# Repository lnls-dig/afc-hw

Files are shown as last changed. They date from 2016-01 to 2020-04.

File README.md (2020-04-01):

# AMC FMC Carrier (AFC)

## Project description

The AMC FMC carrier is partially based on SPEC (supply, WR clocks)
design. It was primarily specified by the Brazilian Synchrotron Light
Laboratory ([LNLS](www.lnls.br)) and designed by Warsaw University of
Technology (WUT) to support quad 16-bit ADC FMC boards for Sirius BPM
electronics. Among many features, the card has very flexible clock
circuit that enables any clock source to be connected to any clock
input, including telecom clock, FMC clocks and
FPGA.

-----

Top view

Bottom view)

-----

## Functional specifications

  - Xilinx Artix-7 200T FFG1156 FPGA (XC7A200T-3FFG1156E)
  - 2 GB DDR3 SDRAM (32-bit interface)
  - 2 high pin count (HPC) slots for 2 single width mezzanines or 1
    double width mezzanine
  - SPI Flash for FPGA configuration
  - SPI Flash for user data storage
  - JTAG multiplexer (SCANSTA) for FMC access
  - Power supply for FPGA, memory, FMCs - programmable VADJ 1.8-3.3V
  - Clock distribution circuit compatible with WR
  - Temperature, voltage and current monitoring for critical power buses
  - Stand-alone power connector
  - Mini-USB connected to the IPMI processor
  - SATA connector for Port2, Port3 with possibility of switching to
    FPGA MGT
  - MGT connected to FMC1, FMC2, Fat Pipe 1, Fat Pipe 2 (optional),
    Port0, Port1, Port2 (optional), Port3 (optional), RTM (optional)
  - EEPROM with MAC and unique ID
  - RTM connector with 8 GTP routed to it. Compatible with rtm-sfp8
    module.

<!-- end list -->

  - [Users](Users)
  - [CERN-ACC-2014-0357](https://cds.cern.ch/record/1977919/files/CERN-ACC-2014-0357.pdf)

-----

## Contacts

### Commercial producers

  - [AMC FMC Carrier – AFC](http://creotech.pl/product-scientific/amc-fmc-carrier-afc) - [Creotech](http://creotech.pl), Poland

### General question about project

  - [Daniel Tavares (LNLS)](mailto:daniel.tavares@lnls.br)
  - [Filip Świtakowski (Creotech)](mailto:filip.switakowski@creotech.pl)

-----

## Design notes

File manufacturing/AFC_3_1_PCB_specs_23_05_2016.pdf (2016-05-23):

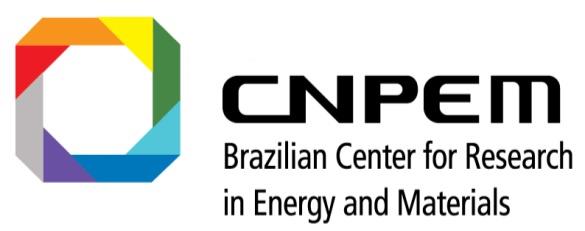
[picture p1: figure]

### Centro Nacional de Pesquisa em Energia e Materiais (CNPEM) Laboratório Nacional de Luz Síncrotron (LNLS) Rua Giuseppe Maximo Scolfaro, 10000, Polo II de Alta Tecnologia Campinas, São Paulo, Brazil CEP 13083-970 – Caixa Postal 6192

# Manufacturing specifications for the AFC_3.1 hardware

# May 2016

# Beam Diagnostics Group (DIG)

BLANK PAGE

Last update: 23 May 2016 - 18:16 | 3

## PCB Fabrication Specification

## Design references

Name | AFC_3.1 | Date: | 05/23/2015
File name
Designers | Fernando Cambauva SantAnna
E-mail | fernando.santanna@lnls.br
Fone | +55 19 3512-5071
Cel | +55 16 99206-8595

## Mechanical characteristics

External size (mm) | 180.6508mm x 148.5508mm
Thickness (mm) | 1.712 mm
Layers | 14
Min track width (mm/mils) | 0.02mm / 2mils
Min Hole size (mm/mils) | 0.15mm / 7.8mils
Laminate | FR-4 – TG150
Pre-preg | FR-4 – TG150

## Finish Copper

External layers (µm) | 35 µm
Holes walls (µm) | 25 µm
Internal Layers-Planes (µm) | 35 µm
Internal Layers-Signals (µm) | 35 µm

## Board finishing requirements

Mask Solder color | Red for prototype and Blue for production
Silkscreen on top layer (color) | White
Silkscreen on bottom layer (color) | White
Surface Finishing | ENIG – Electroless Nickel / Immersion Gold according to IPC-4552
Thickness | Ni: 3 µm min, 6 µm máx. Au: 0.05 µm min, 0.125 µm máx

## Additional Information

Impedance test | No
Packaging requirements | No
Documentation to be delivered | No
Additional control quality requirements | No

| Board Stackup Information

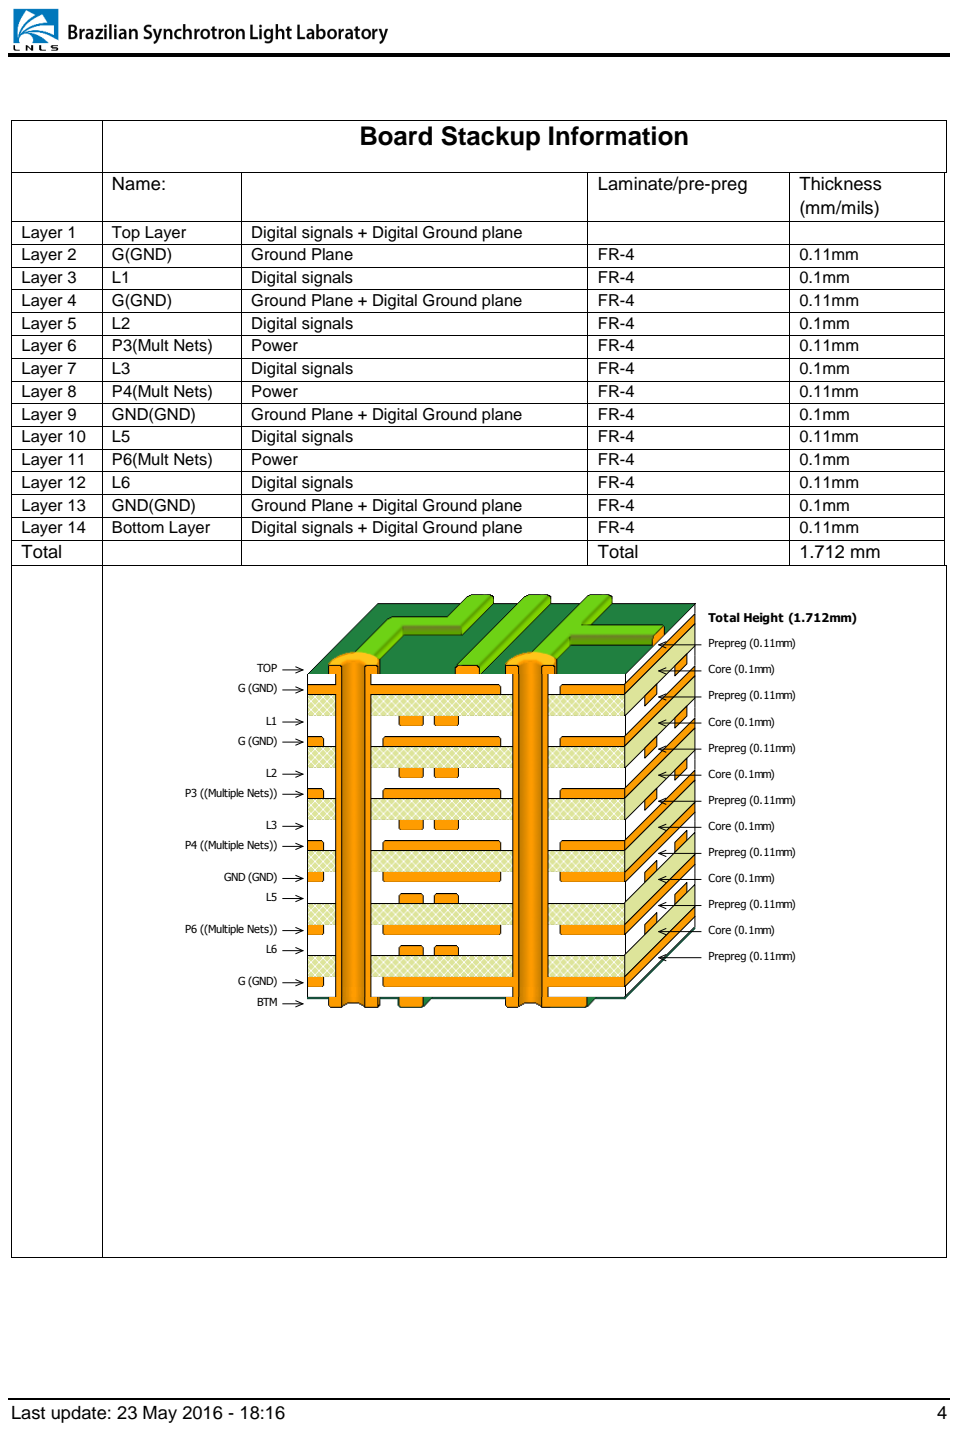
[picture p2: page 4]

Name: | | Laminate/pre-preg | Thickness (mm/mils)

Layer 1 | Top Layer | Digital signals + Digital Ground plane
Layer 2 | G(GND) | Ground Plane | FR-4 | 0.11mm
Layer 3 | L1 | Digital signals | FR-4 | 0.1mm
Layer 4 | G(GND) | Ground Plane + Digital Ground plane | FR-4 | 0.11mm
Layer 5 | L2 | Digital signals | FR-4 | 0.1mm
Layer 6 | P3(Mult Nets) | Power | FR-4 | 0.11mm
Layer 7 | L3 | Digital signals | FR-4 | 0.1mm
Layer 8 | P4(Mult Nets) | Power | FR-4 | 0.11mm
Layer 9 | GND(GND) | Ground Plane + Digital Ground plane | FR-4 | 0.1mm
Layer 10 | L5 | Digital signals | FR-4 | 0.11mm
Layer 11 | P6(Mult Nets) | Power | FR-4 | 0.1mm
Layer 12 | L6 | Digital signals | FR-4 | 0.11mm
Layer 13 | GND(GND) | Ground Plane + Digital Ground plane | FR-4 | 0.1mm
Layer 14 | Bottom Layer | Digital signals + Digital Ground plane | FR-4 | 0.11mm
Total | | | Total | 1.712 mm

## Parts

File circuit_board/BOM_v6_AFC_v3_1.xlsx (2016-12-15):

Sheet: BOM_AFC_v3.1
Prj: | AFC 3.1 | REV.: 6 | data: | 2016-03-04
QTD | Description | Part-number | Manufacturer | Designator
1 | AMC front Panel Double Mid - Aluminum | AMC.0 REL. 2.0 Compliant | CBT Technology
12 | CAEM2917_150UF_4V_20%_LESR015 | EEF-CX0J151R | Panasonic | C86, C115, C135, C473, C539, C41, C50, C55, C64, C230, C231, C528
1 | CAER_470UF_16V_20%_500-1000X1300 | PLF1C471MDO1 | Nichicon | C88
17 | CC0201_0.022UF_6.3V_10%_X5R | GRM033R60J223KE01D | Murata Electronics | C251, C252, C253, C254, C259, C418, C599, C600, C601, C722, C723, C724, C725, C730, C731, C732, C733
376 | CC0201_0.1UF_10V_10%_X5R | GRM033R61A104KE15D | Murata Electronics | C4A, C4B, C6A, C6B, C10A, C10B, C11A, C11B, C15A, C15B, C20, C21, C22, C23, C24, C25, C26, C27, C28, C29, C30, C31, C38, C39, C52, C56, C57, C58, C59, C61, C63, C65, C67, C69, C70, C73, C74, C75, C76, C78, C80, C82, C83, C84, C89, C93, C94, C95, C96, C98, C99, C100, C101, C102, C103, C104, C105, C109, C110, C111, C112, C114, C118, C120, C121, C124, C125, C128, C129, C131, C132, C134, C138, C140, C141, C219, C220, C221, C222, C223, C224, C225, C227, C228, C255, C256, C257, C258, C262, C263, C273, C274, C281, C282, C289, C290, C297, C298, C299, C300, C301, C302, C303, C304, C305, C306, C307, C308, C309, C310, C311, C312, C313, C314, C315, C316, C317, C334, C335, C336, C337, C338, C339, C340, C341, C342, C343, C344, C345, C346, C347, C348, C349, C350, C351, C352, C353, C354, C355, C356, C357, C358, C359, C360, C361, C362, C363, C364, C365, C366, C367, C368, C369, C370, C371, C372, C373, C374, C375, C376, C377, C378, C379, C380, C381, C382, C383, C384, C385, C386, C387, C388, C389, C391, C392, C393, C394, C395, C396, C397, C398, C399, C400, C401, C402, C403, C404, C405, C406, C407, C408, C409, C410, C411, C412, C413, C414, C415, C417, C421, C422, C424, C425, C427, C428, C429, C430, C431, C432, C433, C434, C436, C437, C438, C439, C440, C441, C442, C443, C452, C455, C457, C458, C459, C460, C461, C462, C463, C464, C476, C477, C479, C480, C481, C482, C483, C484, C485, C486, C487, C488, C489, C490, C491, C492, C493, C494, C495, C496, C497, C498, C499, C500, C501, C502, C503, C504, C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
71 | CC0201_0.22UF_6.3V_20%_X5R | C0603X5R0J224M030BB | TDK Corporation | C229, C232, C233, C234, C235, C236, C239, C240, C241, C242, C243, C244, C245, C246, C247, C248, C249, C250, C264, C265, C266, C269, C270, C271, C275, C276, C277, C278, C279, C280, C283, C284, C285, C286, C287, C288, C291, C292, C293, C294, C295, C296, C549, C550, C551, C552, C553, C554, C555, C556, C557, C558, C559, C560, C561, C562, C563, C564, C565, C566, C738, C739, C740, C741, C742, C743, C744, C745, C746, C747, C748
62 | CC0201_0.47UF_6.3V_20%_X5R | C0603X5R0J474M030BC | TDK Corporation | C260, C261, C448, C449, C450, C451, C465, C603, C613, C614, C615, C639, C640, C641, C642, C643, C647, C648, C649, C650, C651, C655, C656, C657, C658, C659, C663, C664, C665, C666, C667, C671, C672, C673, C674, C675, C683, C684, C685, C686, C687, C691, C692, C693, C694, C695, C699, C700, C701, C702, C703, C707, C708, C709, C710, C711, C716, C717, C718, C719, C720, C721
7 | CC0402_0.1UF_16V_10%_X7R | GRM155R71C104KA88D | Murata Electronics | C77, C113, C133, C159, C470, C527, C538
3 | CC0402_10000PF_16V_10%_X7R | GRM155R71C103KA01D | Murata Electronics | C35, C60, C547
3 | CC0402_1000PF_50V_10%_X7R | GRM155R71H102KA01D | Murata Electronics | C166, C634, C635
1 | CC0402_15PF_50V_5%_NPO | CC0402JRNPO9BN150 | Yageo | C208, C435, C444
2 | CC0402_22PF_50V_5%_NPO | CC0402JRNPO9BN220 | Yageo | C18, C19
1 | CC0603_0.022UF_50V_10%_X7R | C1608X7R1H223K080AA | TDK Corporation | C160
2 | CC0603_150PF_50V_5%_NP0 | GRM1885C1H151JA01D | Murata Electronics | C33, C53
54 | CC0603_1UF_25V_10%_X7R | TMK107B7105KA-T | Taiyo Yuden | C2A, C2B, C3A, C3B, C8A, C8B, C9A, C9B, C13A, C13B, C14A, C14B, C16A, C16B, C17A, C17B, C32, C44, C49, C51, C62, C68, C72, C90, C91, C92, C108, C126, C127, C130, C143, C144, C145, C153, C209, C210, C390, C416, C426, C453, C468, C469, C475, C526, C532, C535, C537, C543, C622A, C622B, C623A, C623B, C816, C817
59 | CC0603_4.7UF_10V_10%_X5R | CC0603KRX5R6BB475 | Yageo | C106, C107, C237, C238, C267, C268, C272, C446, C478, C576, C577, C578, C579, C580, C581, C582, C583, C585, C586, C588, C589, C591, C594, C596, C597, C598, C605, C606, C607, C608, C609, C610, C611, C636, C637, C644, C645, C646, C652, C653, C654, C660, C661, C662, C668, C669, C670, C680, C681, C682, C688, C689, C690, C696, C697, C698, C704, C705, C706
24 | CC0805_10UF_25V_10%_X5R | GRM21BR61E106KA73L | Murata Electronics | C12A, C12B, C34, C40, C42, C43, C45, C48, C54, C66, C97, C146, C147, C148, C149, C150, C151, C152, C167, C466, C467, C525, C533, C536
62 | CC1206_22UF_10V_10%_X7R | LMK316AB7226KL-TR | Taiyo Yuden | C1A, C1B, C5A, C5B, C7A, C7B, C46, C47, C71, C79, C81, C85, C87, C116, C117, C119, C122, C123, C136, C137, C139, C142, C154, C155, C156, C157, C158, C161, C162, C163, C164, C165, C168, C169, C170, C171, C172, C173, C174, C175, C176, C177, C419, C420, C423, C454, C455a, C455b, C456, C471, C472, C474, C529, C530, C531, C534, C540, C541, C542, C544, C545, C546
16 | CC1210_100UF_10V_20%_X5R | GRM32ER61A107ME20L | Murata Electronics | C226, C447, C587, C592, C593, C602, C612, C638, C676, C677, C678, C679, C712, C713, C714, C715
1 | CONN GUIDE MODULE KEYED 1POS | 5120913-1 | TE Connectivity AMP Connectors | J12
1 | CONN HDR 2X5 0.100" SMT | 54202-G0805LF | FCI | JP1
1 | CONN HEADER .050" 2X5 DL PCB AU | GRPB052VWVN-RC | Sullins Connector Solutions | JP2
1 | CONN HEADER 14POS 2MM VERT SMD | 87832-1420 | Molex | J6
1 | CONN HEADER 4POS 4.2MM VERT TIN | 39-28-1043 | Molex | J4
2 | CONN RCPT 60POS 3PAIR R/A HM-ZD | 6469081-1 | TE Connectivity AMP Connectors | J1, J2
2 | CONN RCPT STD MICRO USB TYPE AB | 10104111-0001LF | FCI | CON2A, CON2B
4 | CONN UMC JACK STR 50 OHM SMD | U.FL-R-SMT-1(10) | Hirose Electric | J7, J11, J16, J17
2 | CONN, VITA 57 FMC, RCPT, 400POS, 10ROW | ASP-134486-01 | SAMTEC | J15A, J15B
1 | CRYSTAL 32.7680KHZ 12.5PF SMD | ABS25-32.768KHZ-T | Abracon | X3
3 | DIODE SCHOTTKY 40V 750MA SOD323 | BAT165E6327 | Infineon Technologies | D1, D3, D4
3 | DIODE SCHOTTKY 60V 1A DO214AC | SS16-E3/61T | Vishay | D2, D5, D6
1 | F_PTC_9.5x6mm | MF-SM250-2-99 | Bourns Inc. | F3
4 | FERRITE BEAD 100 OHM 8A SMD 1812 | 74279226101 | Wurth Electronics | FB5, FB6, FB7, FB8
6 | FERRITE CHIP 220 OHM 0805 | BLM21PG221SN1D | Murata Electronics | L9, L14, L17, L18, L19, L21
6 | FIXED IND 1.5UH 11A 10.67 MOHM | SPM6530T-1R5M100 | TDK Corporation | L1, L3, L5, L6, L15, L16
4 | FIXED IND 1UH 1.8A 52 MOHM SMD | ELLVGG1R0N | Panasonic Electronic | L10, L11, L12, L13
2 | FIXED IND 3.3UH 5.3A 15 MOHM SMD | 74456033 | Wurth Electronics | L2, L7
1 | FIXED IND 440NH 30A 0.32 MOHM | PA0513.441NLT | Pulse Electronics | L8
1 | Heat sink BGA 35x35(44.9)mm | ATS-50350B-C1-R0 | Advanced Thermal Solutions | HS1
2 | IC BUS TRANSCVR 8BIT 24QFN | SN74AVC8T245RHLR | Texas Instruments | IC40, IC41
8 | IC BUS TRANSCVR TRI-ST SOT-563 | SN74AVC1T45DRLR | Texas Instruments | IC28, IC29, IC34, IC35, IC36, IC37, IC38, IC39
1 | IC CLK GEN 1:4 LOW JITTER 32-QFN | CDCM61004RHBT | Texas Instruments | IC50
1 | IC CROSSPOINT SWIT 16X16 100TQFP | ADN4604ASVZ | Analog Devices | IC8
6 | IC CURRENT MONITOR 1% 10MSOP | INA220AIDGST | Texas Instruments | IC19, IC20, IC21, IC59, IC60, IC61
2 | IC DAC 16BIT BUFF V-OUT 8MSOP | AD5662BRMZ-1 | Analog Devices | IC52, IC53
1 | IC EEPROM 2KBIT 1MHZ 8TSSOP | AT24MAC602-XHM-T | Atmel | IC27
2 | IC FLASH 128MBIT 50MHZ 8VDFPN | M25P128-VME6TGB | Micron Technology | IC13, IC64
1 | IC FPGA 500 I/O 1156FCBGA | XC7A200T-3FFG1156E | Xilinx | IC2
1 | IC MCU ARM 128KB FLASH 100LQFP | LPC1764FBD100 | NXP Semiconductors | IC1
2 | IC M-LVDS RCVR QUAD 48VQFN | SN65MLVD040RGZT | Texas Instruments | IC22, IC23
1 | IC MPU RESET CIRC 2.93V SOT143-4 | PT7M7811STBEX | Pericom | IC58
1 | IC MPU RESET CIRC 2.93V SOT23 | STM809SWX6F | STMicroelectronics | IC3
1 | IC MUX 8CH I2C BUS 24-HVQFN | PCA9547BS,118 | NXP Semiconductors | IC79
2 | IC MUX UHS NONINVERT 2INP SC70-6 | NC7SZ157P6X | Fairchild Semiconductor | IC80, IC81
1 | IC MUX/DEMUX TRIPLE 2X1 16SOIC | 74HC4053D,653 | NXP Semiconductors | IC73
1 | IC POT DGTL DUAL 10K 8BIT 14SOIC | AD8402ARZ1 | Analog Devices | IC11
1 | IC REDRIVER I2C 1CH 8VSSOP | PCA9517DGKR | Texas Instruments | IC42
4 | IC REDRIVER LVDS 1CH 1.6GBPS US8 | FIN1101K8X | Fairchild Semiconductor | IC46, IC47, IC49, IC66
1 | IC REG BUCK ADJ 20A SYNC 22SON | TPS53353DQPT | Texas Instruments | IC14
2 | IC REG BUCK ADJ 3A SYNC 8SOIC | NCP3170ADR2G | ON Semiconductor | IC55, IC57
3 | IC REG CTRLR BUCK PWM 24-VQFN | TPS53126RGET | Texas Instruments | IC10, IC12, IC43
1 | IC REG LDO 3.3V 0.8A DPAK | LD1117DT33CTR | STMicroelectronics | IC74
1 | IC REG LDO 3V 0.15A SOT23-5 | LP5951MF-3.0/NOPB | Texas Instruments | IC51
1 | IC RTC CLK/CALENDAR I2C 8-SOIC | MCP79410-I/SN | Microchip Technology | IC9
1 | IC SCAN BRIDGE MULTIDROP 48TSSOP | SCANSTA111MT/NOPB | Texas Instruments | IC6
1 | IC SINK/SOURCE DDR REG 10-SON | TPS51200DRCT | Texas Instruments | IC44
2 | IC USB-TO-UART BRIDGE 28VQFN | CP2102-GM | Silicon Labs | IC62A, IC62B
4 | IC VOLT-LEVEL TRANSLATOR 14TSSOP | TXB0104PWR | Texas Instruments | IC68, IC69, IC70, IC71
2 | IC VOLT-LEVEL TRANSLATOR SM8 | PCA9306DCTR | Texas Instruments | IC25, IC56
1 | IC VREF SHUNT ADJ SOT23-3 | TS3431ILT | STMicroelectronics | IC45
1 | IC VREF SHUNT ADJ SOT23-3 | TL431QDBZT | Texas Instruments | IC54
1 | LED CHIP GREEN CLEAR RA 0603 SMD | HSME-C120 | Avago Technologies | LDx
1 | LED CHIP INGAN BLU SIDE EMIT SMD | HSMR-C120 | Avago Technologies | LDy
15 | LED CHIP RED CLEAR RT ANG 0603 SMD | HSMC-C120 | Avago Technologies | LED3, LED4, LED5, LED6, LED7, LED8, LED9, LED10, LED11, LED12, LED13, LED14, LED15, LED16, LED17
1 | LED RED/GRN/BLUE 1204 SMD | OVSRRGBCC3TM | TT Electronics | LD1
4 | MEM Chip DDR3 SDRAM 4G-Bit 512Mx8 1.35V(1.5 Compatibile) 78-Pin FBGA | MT41K512M8RH-125:E | MT41K512M8RH-125:E | IC15, IC16, IC24, IC26
6 | MOSFET 2N-CH 20V 10A/12A 8-SOIC | IRF9910TRPbF | Infineon Technologies | T1, T2, T3, T4, T5, T6
7 | MOSFET N-CH 50V 220MA SOT-23 | BSS138 | Fairchild Semiconductor | Q3, Q4, Q7, Q9, Q10, Q11, Q14
3 | MOSFET P-CH 30V 20A 8-SOIC | IRF9310TRPbF | Infineon Technologies | Q1, Q2, Q13
1 | OSC XO 10-280MHZ LVPECL SMD | Si570BBC000121DG | Silicon Labs | OSC4
1 | OSC_20MHZ_IQD_LF VCXO026156 | LF VCXO026156 | IQD FREQUENCY PRODUCTS | OSC2
3 | PTC SMD 1812 0.5A 16V | PTS181216V050 | Eaton Bussman | F1, F2, F4
1 | Quartz crystal SMD 5*3.2mm 8.000MHz | 7A-8.000MAAJ-T | TXC | X1
2 | R0201_49R9_1%_0.05W_200PPM | ERJ-1GEF49R9C | Panasonic Electronic | R143, R181
18 | R0402_0R_JUMPER_0.1W | RC0402JR-070RL | Yageo | R70, R80, R124, R135, R136, R137, R139, R140, R146, R215, R253, R258, R289, R290, R293, R306, R318, R319
15 | R0402_100K_1%_0.0625W_100PPM | RC0402FR-07100KL | Yageo | R45, R52, R64, R106, R109, R110, R120, R121, R179, R209, R210, R269, R297, R301, R302
37 | R0402_100R_1%_0.0625W_100PPM | RC0402FR-07100RL | Yageo | R7, R8, R9, R10, R11, R12, R13, R14, R15, R16, R17, R18, R96, R118, R142, R148, R149, R150, R151, R152, R153, R154, R155, R156, R157, R207, R208, R217, R226, R227, R229, R230, R231, R239, R335, R345, R346
60 | R0402_10K_1%_0.0625W_100PPM | RC0402FR-0710KL | Yageo | R2, R3, R4, R5, R6, R19, R37, R38, R39, R40, R55, R57, R58, R59, R60, R61, R71, R78, R79, R82, R85, R92, R97, R98, R99, R100, R101, R102, R103, R104, R105, R114, R117, R122, R123, R141, R145, R147, R158, R159, R162, R164, R180, R222, R225, R238, R246, R255, R264, R265, R268, R270, R280, R281, R282, R305, R309, R310, R326, R350
16 | R0402_10R_1%_0.0625W_100PPM | RC0402FR-0710RL | Yageo | R125, R126, R129, R130, R133, R286, R291, R292, R294, R295, R296, R298, R300, R303, R304, R351
12 | R0402_1K_1%_0.0625W_100PPM | RC0402FR-071KL | Yageo | R165, R220, R221, R232, R233, R234, R235, R236, R237, R272, R287, R288
3 | R0402_1K3_1%_0.1W_100PPM | ERJ-2RKF1301X | Panasonic Electronic | R54, R86, R91
7 | R0402_240R_1%_0.0625W_100PPM | RC0402FR-07240RL | Yageo | R144, R167, R168, R216, R218, R219, R228
34 | R0402_2K2_1%_0.0625W_100PPM | RC0402FR-072K2L | Yageo | R36, R47, R81, R83, R119, R169, R170, R171, R172, R173, R174, R176, R178, R214, R244, R271, R273A, R273B, R274A, R274B, R275A, R275B, R276A, R276B, R283, R307, R308, R313, R314, R331, R332, R338, R347, R348
11 | R0402_330R_1%_0.0625W_100PPM | CRCW0402330RFKED | Vishay Dale | R23, R24, R132, R161, R175, R213, R277, R278, R279, R311, R312
4 | R0402_33R_1%_0.0625W_100PPM | RC0402FR-0733RL | Yageo | R284A, R284B, R285A, R285B
27 | R0402_43R_1%_0.0625W_100PPM | CRCW040243R0FKED | Vishay Dale | R163, R177, R182, R183, R184, R185, R186, R187, R188, R189, R190, R191, R192, R193, R194, R195, R196, R197, R198, R199, R200, R201, R202, R203, R204, R205, R206
2 | R0402_49R9_1%_0.0625W_100PPM | CRCW040249R9FKED | Vishay Dale | R51, R211
10 | R0402_4K7_1%_0.0625W_100PPM | RC0402FR-074K7L | Yageo | R20, R21, R22, R49, R50, R69, R127, R131, R160, R166
8 | R0402_510R_1%_0.0625W_100PPM | RC0402FR-07510RL | Yageo | R65, R66, R74, R76, R77, R88, R93, R256
1 | R0603_169K_1%_0.1W_100PPM | CRCW0603169KFKEA | Vishay Dale | R112
3 | R0603_1K5_1%_0.1W_100PPM | RC0603FR-071K5L | Yageo | R46, R247, R248
1 | R0603_1K6_1%_0.1W_100PPM | CRCW06031K60FKEA | Vishay Dale | R48
2 | R0603_24K9_0.1%_0.0625W_10PPM | PCF0603-12-24K9BT1 | TT Electronics/Welwyn | R43, R62
2 | R0603_2K49_0.1%_0.0625W_25PPM | RNCS0603BKE2K49 | Stackpole Electronics Inc. | R44, R63
3 | R0603_2R_1%_0.1W_200PPM | RC0603FR-072RL | Yageo | R111, R327, R328
3 | R0603_3K3_1%_0.1W_100PPM | RC0603FR-073K3L | Yageo | R72, R115, R116
2 | R0603_453R_0.1%_0.1W_25PPM | RG1608P-4530-B-T5 | Susumu | R262, R263
3 | R0603_4K3_1%_0.1W_100PPM | RC0603FR-074K3L | Yageo | R53, R84, R90
7 | R0603_5K1_1%_0.1W_100PPM | RC0603FR-075K1L | Yageo | R41, R42, R73, R87, R95, R223, R259
1 | R0603_75K_1%_0.1W_100PPM | ERJ-3EKF7502V | Panasonic Electronic | R108
2 | R0603_910R_1%_0.1W_100PPM | ERJ-3EKF9100V | Panasonic Electronic | R260, R261
2 | R1206_100K_1%_0.25W_100PPM | ERJ-8ENF1003V | Panasonic Electronic | R320, R321
1 | R1206_3R_1%_0.25W_200PPM | RC1206FR-073RL | Yageo | R113
8 | R2512_0.001R_1%_2W_275PPM | WSL25121L000FEA | Vishay Dale | R75, R89, R94, R257, R266, R267
4 | SENSOR TEMPERATURE I2C 8SOIC | LM75AIM/NOPB | Texas Instruments | IC30, IC31, IC32, IC33
1 | SENSOR TEMPERATURE SMBUS 6TDFN | MAX6642ATT90-T | Maxim Integrated | IC18
1 | SWITCH DETECTOR SPST TOP ACT 5V | HDT0001 | C&K Components | PB1
1 | SWITCH TACTILE Push Button 6X6mm | SKHHLQA010 | ALPS | S1
3 | TRANS NPN 45V 0.1A SOT-23 | BC847B,215 | NXP Semiconductors | Q5, Q6, Q12
2 | TVS DIODE 5.5VWM SOT143B | PRTR5V0U2X,215 | NXP Semiconductors | D7A, D7B
3 | TVS DIODE 6.2VWM 9VC 6TSOP | BZA462A,115 | NXP Semiconductors | IC4, IC5, IC7
1 | VC-TCXO SMD 3V 25.000MHz 3.2x5mm | VM53S3-25.000-2.5/-30+75 | Mercury | OSC5

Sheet: Plan1
C4A
C4B
C6A
C6B
C10A
C10B
C11A
C11B
C15A
C15B
C20
C21
C22
C23
C24
C25
C26
C27
C28
C29
C30
C31
C38
C39
C52
C56
C57
C58
C59
C61
C63
C65
C67
C69
C70
C73
C74
C75
C76
C78
C80
C82
C83
C84
C89
C93
C94
C95
C96
C98
C99
C100
C101
C102
C103
C104
C105
C109
C110
C111
C112
C114
C118
C120
C121
C124
C125
C128
C129
C131
C132
C134
C138
C140
C141
C219
C220
C221
C222
C223
C224
C225
C227
C228
C255
C256
C257
C258
C262
C263
C273
C274
C281
C282
C289
C290
C297
C298
C299
C300
C301
C302
C303
C304
C305
C306
C307
C308
C309
C310
C311
C312
C313
C314
C315
C316
C317
C334
C335
C336
C337
C338
C339
C340
C341
C342
C343
C344
C345
C346
C347
C348
C349
C350
C351
C352
C353
C354
C355
C356
C357
C358
C359
C360
C361
C362
C363
C364
C365
C366
C367
C368
C369
C370
C371
C372
C373
C374
C375
C376
C377
C378
C379
C380
C381
C382
C383
C384
C385
C386
C387
C388
C389
C391
C392
C393
C394
C395
C396
C397
C398
C399
C400
C401
C402
C403
C404
C405
C406
C407
C408
C409
C410
C411
C412
C413
C414
C415
C417
C421
C422
C424
C425
C427
C428
C429
C430
C431
C432
C433
C434
C436
C437
C438
C439
C440
C441
C442
C443
C452
C455
C457
C458
C459
C460
C461
C462
C463
C464
C476
C477
C479
C480
C481
C482
C483
C484
C485
C486
C487
C488
C489
C490
C491
C492
C493
C494
C495
C496
C497
C498
C499
C500
C501
C502
C503
C504
C505
C506
C507
C508
C509
C510
C511
C512
C513
C514
C515
C516
C517
C518
C519
C520
C521
C522
C523
C524
C548
C567
C568
C569
C570
C571
C572
C573
C574
C575
C584
C590
C595
C595x
C604
C616
C617
C618
C619
C620
C621
C624A
C624B
C625
C726
C727
C728
C729
C734
C735
C736
C737
C749
C750
C751
C752
C753
C755
C756
C757
C758
C759
C760
C762
C766
C768
C769
C770
C771
C772
C773
C774
C775
C776
C777
C778
C779
C780
C781
C782
C783
C784
C785
C786
C787
C788
C789
C790
C791
C792
C793
C794
C795
C796
C797
C798
C799
C800
C801
C802
C803
C804
C805
C806
C807
C808
C809
C810
C811
C812
C813
C814
C815
C838
C839
C875
C882
C888
CC524

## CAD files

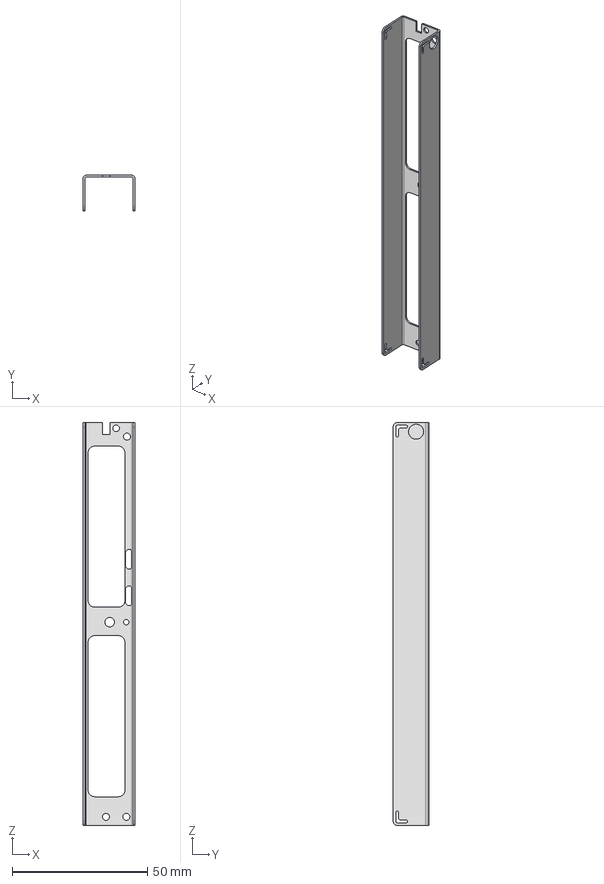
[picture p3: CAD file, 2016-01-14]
mechanical/AMC_FMC_Carrier_35u_tears.stp
19.2 x 13.2 x 148.8 mm

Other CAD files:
mechanical/AMC_PANEL_SILK.dwg
mechanical/AMC_FMC_Carrier_35u_tears.igs

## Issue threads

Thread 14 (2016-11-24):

### ISSUE TITLE
Replace D5 and D6 for a single higher forward current diode

### ISSUE THREAD

**Issue by henrique-silva** [lnls-dig/afc-hw#14]
The SS16 schottky diode has a forward current limit set in 1A, which is less than needed for the AFC board fully operate with both FMC connected when powered from the ATX stand-alone connector.

Using 2 diodes in parallel is dangerous because if they have a slight unbalacing, one of them will start to drive more current and, consequently, heat more. The heating in a diode makes it drive even more current, resulting in a positive current feedback that ends with the diode burning up.

**Comment by aylons** [comment]
I agree.

To substitute it, I suggest a diode from this list:

http://www.digikey.com/product-search/en/discrete-semiconductor-products/diodes-rectifiers-single/1376383?k=&pkeyword=&pv1291=2025&pv1291=7351&pv1291=2050&FV=1140003%2Ce480002%2Ce480006%2Ce480009%2Ce480014%2Ce48001c%2Ce480020%2Ce480023%2Ce480024%2Ce480027%2Ce480028%2Ce480029%2Ce48002f%2Ce480038%2Ce48003f%2Ce480062%2Ce4800c4%2Ce4800c7%2Ce4800c9%2Ce4800ca%2Ce4800cb%2Ce4800cd%2Ce4800cf%2Ce4800d0%2Ce4800d2%2Ce4800fa%2Ce480136%2Ce480138%2Ce480139%2Ce48016e%2Ce48016f%2Ce4801c7%2Ce500001%2Ce500002%2Ce500003%2Ce500005%2Ce500006%2Ce500007%2Ce50000a%2Ce50000b%2Ce50000c%2Ce50000d%2Ce50000e%2Ce50000f%2Ce500010%2Ce500011%2Ce500012%2Ce500013%2Ce500014%2Ce500015%2Ce500016%2Ce500017%2Ce500018%2Ce500019%2Ce50001a%2Ce50001b%2Ce50001c%2Ce50001d%2Ce50001e%2Ce50001f%2Ce500020%2Ce500021%2Ce500022%2Ce500023%2Ce500024%2Ce500025%2Ce500027%2Ce500028%2Ce500029%2Ce50002a%2Ce50002b%2Ce50002c%2Ce50002d%2Ce50002e%2Ce50002f%2Ce500030%2Ce500032%2Ce500034%2Ce500035%2Ce500037%2Ce500038%2Ce500039%2Ce50003a%2Ce50003b%2Ce50003c%2Ce50003d%2Ce50003e%2Ce50003f%2Ce500040%2Ce500041%2Ce500042%2Ce500043%2Ce500044%2Ce500045%2Ce50004a%2Ce50004e%2Ce500051%2Ce500058%2Ce50005c%2Ce500061%2Ce500063%2Ce50006b%2Ce50006e%2Ce50006f%2Ce500076%2Ce500077%2Ce500078%2Ce500079%2Ce50007a%2Ce50007b%2Ce50007e%2Ce500080%2Ce500082%2Ce500083%2Ce500084%2Ce50008b%2Ce50008c%2Ce50008f%2Ce500090%2Ce500092%2Ce500093%2Ce500094%2Ce500095%2Ce500096%2Ce500097%2Ce500098%2Ce500099%2Ce50009a%2Ce50009d%2Ce50009e%2Ce5000a0%2Ce5000a1%2Ce5000a2%2Ce5000a3%2Ce5000a4%2Ce5000a5%2Ce5000a6%2Ce5000a8%2Ce5000a9%2Ce5000aa%2Cfff40015%2Cfff8007f%2C40014d%2C400389%2C400ab1&mnonly=0&newproducts=0&ColumnSort=1000011&page=1&stock=1&quantity=0&ptm=0&fid=0&pageSize=250

I actually liked this option from AVX, which is small and fits the bill:

http://www.digikey.com/product-detail/en/avx-corporation/SD2114S040S8R0/478-7817-2-ND/3749521

However, maybe a more standard and bigger DO-214 (SMB or SMC) would be a better option, so we can change PN or manufacturer later.

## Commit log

2013-08-26 new repo initialization for rev1 and rev2 production files
    [AMC-SATA.SchDoc, AMC_Connector.SchDoc, AMC_FMC_Carrier v2.PrjPcb, AMC_FMC_Carrier v2.csv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]
2013-10-25 afc v3 init repo
    [AMC-SATA.SchDoc, AMC_Connector.SchDoc, AMC_FMC_Carrier v3.PrjPcb, AMC_FMC_Carrier.SchDoc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]
2013-11-03 fixed several issues wrong voltage measurement on FMC P12V - before the switch Added JTAG support for RTM_CON Added RTM power switches and I2C buffer moved both USB ports to the front panel swapped G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
    [AMC_FMC_Carrier.SchDoc, CPU.SchDoc, Clock_management.SchDoc, FMC_HPC1.SchDoc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]
2013-11-04 design ready for schematic review
    [AMC_FMC_Carrier v3.PrjPcb, Clock_management.SchDoc, FPGA.SchDoc, FPGA_MGT.SchDoc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]
2013-11-05 added option description to the MGT schematic detected swapped RTM connectors - some work need to be done on layout version without polygons to reduce PCB size and to make checking easier
    [AMC_Connector.SchDoc, AMC_FMC_Carrier v3.PrjPcb, FPGA_MGT.SchDoc]
2013-11-24 added low jitter WR clock output (UFL connectors) inverted all HPC lines
    [Clock_WR.SchDoc, FMC_HPC1.SchDoc, FMC_HPC2.SchDoc, FPGA_MGT.SchDoc]
2013-11-25 MGT connection upgrade - AMC Ports 12-15 added, P3V3 aux regulator added in stand-alone mode Port0/1 and 2-lane FP2 operation now possible quad 116 connected to the clock crossbar lot of small bugs f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
    [AMC-SATA.SchDoc, AMC_Connector.SchDoc, AMC_FMC_Carrier v3.PrjPcb, AMC_FMC_Carrier.SchDoc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]
2014-01-01 unified all RC All RC come from CERN library Seriously limited BOM Almost all issues solved PCB - acute angles removed improved plane layout- limited cutouts over high speed signals added OutJob file
    [AMC-SATA.SchDoc, AMC_Connector.SchDoc, AMC_FMC_Carrier v3.PrjPcb, AMC_FMC_Carrier.SchDoc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]
2014-01-29 added low jitter clock bypass
    [AMC_FMC_Carrier v3.PrjPcb, Clock_management.SchDoc, Low_jitter_CLK_bypass.SchDoc]
2014-02-10 added low jitter clock bypass - implemented on PCB
    [AMC_FMC_Carrier v3.PrjPcb, AMC_FMC_Carrier.SchDoc, CPU.SchDoc, Clock_management.SchDoc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]
2014-02-21 100% of layout done, some cosmetic changes may be needed. 0 DRC errors fixed some bugs
    [FMC_Clocks.SchDoc, Low_jitter_CLK_bypass.SchDoc]
2014-02-21 version compatible with AD10
    [AMC_FMC_Carrier.SchDoc]
2014-04-04 fixed some mechanical issues. Added OHL license on the schematics updated mounted/not mounted designators.
    [AMC-SATA.SchDoc, AMC_FMC_Carrier v3.PrjPcb, AMC_FMC_Carrier.SchDoc, Clock_management.SchDoc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]
2014-05-16 added PCB file to the commit
2014-08-01 Added schematics & pcb pdf
    [Low_jitter_CLK_bypass.SchDoc]
2015-06-03 added v.3.1
    [AMC-SATA.SchDoc, AMC_Connector.SchDoc, AMC_FMC_Carrier v2.csv, AMC_FMC_Carrier v2.xlsx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]
2016-01-14 New folder and files structure
    structure following the pattern DIG
    [AMC-SATA.SchDoc, AMC_CPU_COM_EXPRESS.igs, AMC_CPU_COM_EXPRESS.stp, AMC_CPU_COM_EXPRESS_silk.dwg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]
2016-02-05 remove mechanical design files
    leave only files related to the AFC project itself
    [AMC_CPU_COM_EXPRESS.igs, AMC_CPU_COM_EXPRESS.stp, AMC_CPU_COM_EXPRESS_silk.dwg, RTM_SFP.igs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]
2016-02-05 modify folders' structure
    keep coherence with other open-hardware projects
    [AMC-SATA.SchDoc, AMC_Connector.SchDoc, AMC_FMC_Carrier v3.PrjPcb, AMC_FMC_Carrier.SchDoc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]
2016-02-05 make flat files structure inside circuit_board folder
    [AMC-SATA.SchDoc, AMC_Connector.SchDoc, AMC_FMC_Carrier.PrjPcb, AMC_FMC_Carrier.SchDoc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]
2016-02-05 rename BOM file
    avoid version name on filename
    [BOM_AFC.xlsx]
2016-11-10 Removed FMC clock bypass and associated signals
    [AMC_FMC_Carrier.SchDoc, CPU.SchDoc, Clock_WR.SchDoc, Clock_management.SchDoc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]
2016-11-10 Removed AVR as an MMC controller from the schematics
    [CPU.SchDoc]
2016-11-17 Changed CPU to LPC1768, updated library
    [CPU.SchDoc]
2016-11-17 Changed red led part
    [CPU.SchDoc]
2016-11-21 New debug/programming features for MMC
    Added newn JTAG switch and USB Uart programmer. Reassigned MMC pins accordingly.
    [AMC_FMC_Carrier.PrjPcb, AMC_FMC_Carrier.SchDoc, CPU.SchDoc, Clock_WR.SchDoc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]
2016-11-23 Changed LPC reset circuit and corrected AMC Enable connection
    [CPU.SchDoc]
2016-11-23 Changed RTM_PS# and EN_I2C_RTM so they can have different directions
    Fixes #1428
    [CPU.SchDoc]
2016-11-23 Changed UART serial resistors for lower value.
    This should avoid problem in circuits with 10k pull ups.
    [USB_UART.SchDoc]
2016-11-24 Corrected RTM harness connection.
    As discussed in #1434 (note-3) issues.
    [JTAG_Configuration.SchDoc]
2016-11-24 Changed Flash memory to N25Q, removed extras
    Fixes #1433
    [FPGA.SchDoc]
2016-11-24 Changed diodes from P12V_AUX to single diode
    Fixes #1439
    [Power_Management.SchDoc]
2016-11-24 Changed fuses for better availability.
    [Power_Management.SchDoc]
2016-11-24 Added diode to prevent reverse current from P3V3MP and P12V
    Fixes #1440
    [Power_Management.SchDoc]
2016-11-29 First power supply changes, refactor for readability
    [AMC_FMC_Carrier.SchDoc, CPU.SchDoc, Connector_Power.SchDoc, JTAG_Configuration.SchDoc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]
2016-12-02 Updated MMC power management
    Added latches for PM control (fixes #1438)
    Used LPC1768 ADCs for extra voltage monitoring (fixes #1432 and #1111)
    This required some pin changes in the LPC1768. Also, did some improvements in CPU.SchDoc layout.
    [AMC_Connector.SchDoc, AMC_FMC_Carrier.PrjPcb, AMC_FMC_Carrier.SchDoc, CPU.SchDoc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]
2016-12-02 Standardized the TVS to all connectors.
    [AMC_Connector.SchDoc, CPU.SchDoc, Power_Management.SchDoc, USB_UART.SchDoc]
2016-12-02 Added MMC-controlled switch to RTM 3V3MP
    [AMC_FMC_Carrier.SchDoc, CPU.SchDoc, Connector_Power.SchDoc, Power_Management.SchDoc]
2016-12-15 update BOM file
    new BOM file (removed DNP and "nm")
    [BOM_AFC.xlsx, BOM_v6_AFC_v3_1.xlsx]
2020-05-12 Removed small unecessary openings in the solder mask
